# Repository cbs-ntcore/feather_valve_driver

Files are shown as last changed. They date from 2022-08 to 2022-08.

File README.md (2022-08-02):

Feather compatible 16 channel valve driver.

This was designed for 12 volt Lee valves.

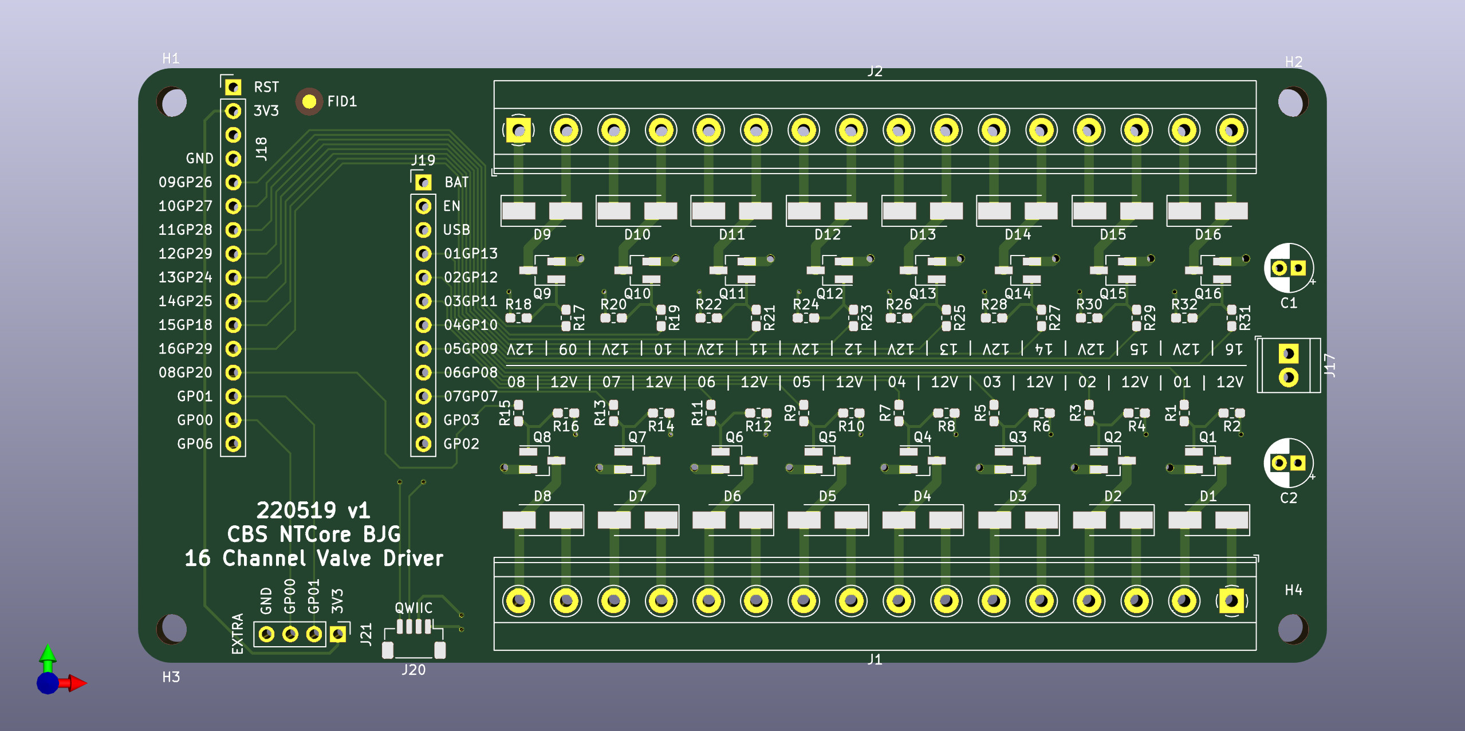
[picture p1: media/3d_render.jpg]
PCB 3D render


See [errata](/electronics/feather_valve_driver/ERRATA) for current minor electronic issues.

A simple 3d printed baseplate is included that supports the Lee valves:

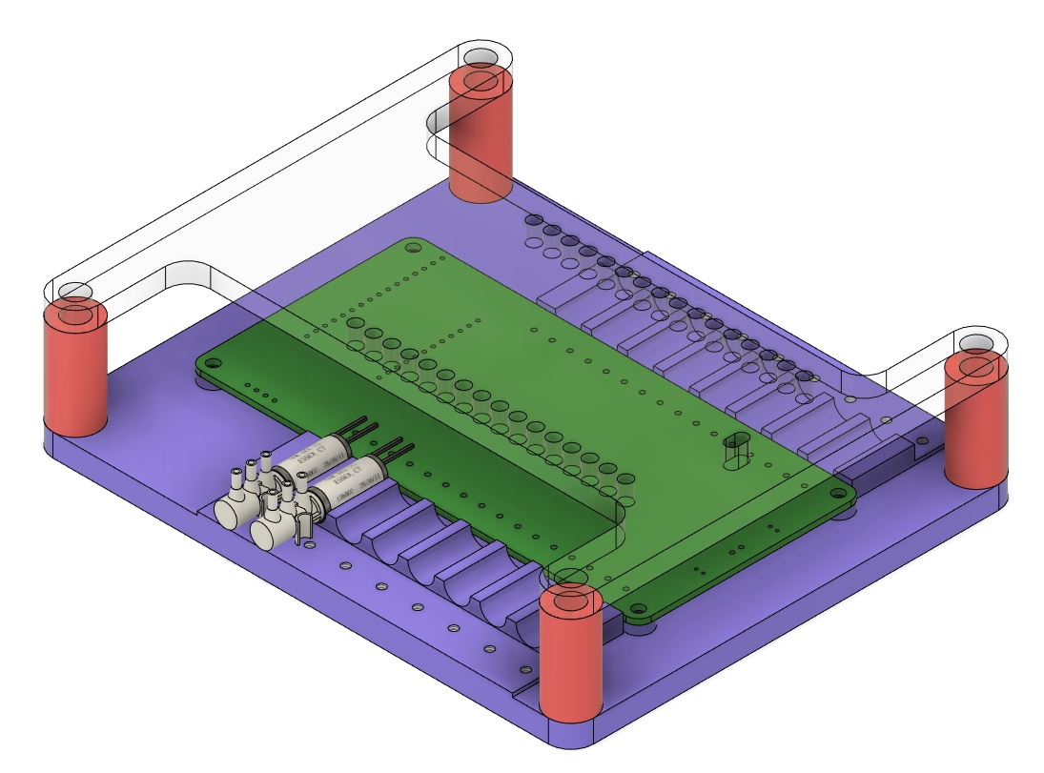
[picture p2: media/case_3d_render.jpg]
Baseplate 3D render


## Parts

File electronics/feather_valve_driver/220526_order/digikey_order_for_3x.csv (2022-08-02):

Index | Quantity | Part Number | Manufacturer Part Number | Description | Customer Reference | Available | Backorder | Unit Price | Extended Price USD
1 | 130 | 1655-S1MCT-ND | S1M | DIODE GEN PURP 1KV 1A SMA |  | 130 | 0 | 0.07000 | 9.10
2 | 130 | 31-DMN3731U-7CT-ND | DMN3731U-7 | MOSFET N-CH 30V 900MA SOT23 |  | 130 | 0 | 0.11850 | 15.41
3 | 130 | RMCF0603FT100RCT-ND | RMCF0603FT100R | RES 100 OHM 1% 1/10W 0603 |  | 130 | 0 | 0.00680 | 0.88
4 | 130 | RNCP0603FTD10K0CT-ND | RNCP0603FTD10K0 | RES 10K OHM 1% 1/8W 0603 |  | 130 | 0 | 0.02480 | 3.22
5 | 10 | A134903-ND | 1-282837-6 | TERM BLK 16P SIDE ENT 5.08MM PCB |  | 10 | 0 | 6.76200 | 67.62
6 | 10 | ED10561-ND | OSTVN02A150 | TERM BLK 2P SIDE ENT 2.54MM PCB |  | 10 | 0 | 0.59600 | 5.96
7 | 10 | 493-12902-1-ND | UVY1E101MDD1TD | CAP ALUM 100UF 20% 25V RADIAL |  | 10 | 0 | 0.27100 | 2.71

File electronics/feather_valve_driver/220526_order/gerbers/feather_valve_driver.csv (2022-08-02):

Id | Designator | Package | Quantity | Designation | Supplier and ref
1 | FID1 | Fiducial_1.5mm_Mask3mm | 1 | Fiducial
2 | H4,H3,H2,H1 | MountingHole_3.2mm_M3 | 4 | MountingHole
3 | C2,C1 | CP_Radial_D5.0mm_P2.00mm | 2 | CP
4 | J18 | PinHeader_1x16_P2.54mm_Vertical | 1 | Conn_01x16
5 | R32,R30,R28,R26,R24,R22,R20,R18,R16,R14,R12,R10,R8,R6,R4,R2 | R_0603_1608Metric_Pad1.05x0.95mm_HandSolder | 16 | 10k
6 | R31,R29,R27,R25,R23,R21,R19,R17,R15,R13,R11,R9,R7,R5,R3,R1 | R_0603_1608Metric_Pad1.05x0.95mm_HandSolder | 16 | 100
7 | Q16,Q15,Q14,Q13,Q12,Q11,Q10,Q9,Q8,Q7,Q6,Q5,Q4,Q3,Q2,Q1 | SOT-23_Handsoldering | 16 | Q_NMOS_GSD
8 | J21 | PinHeader_1x04_P2.54mm_Vertical | 1 | EXTRA
9 | J20 | JST_SH_BM04B-SRSS-TB_1x04-1MP_P1.00mm_Vertical | 1 | QWIIC
10 | J19 | PinHeader_1x12_P2.54mm_Vertical | 1 | Conn_01x12
11 | J17 | TerminalBlock_TE_282834-2_1x02_P2.54mm_Horizontal | 1 | Conn_01x02
12 | J2,J1 | TerminalBlock_Phoenix_MKDS-3-16-5.08_1x16_P5.08mm_Horizontal | 2 | Conn_01x16
13 | D16,D15,D14,D13,D12,D11,D10,D9,D8,D7,D6,D5,D4,D3,D2,D1 | D_SMA_Handsoldering | 16 | D

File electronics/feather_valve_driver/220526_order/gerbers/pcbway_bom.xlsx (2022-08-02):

 |  |  | xxxx xxxx xxxxx xxPCS BOM (Sample Bill of Materials)
Item # | *Designator | *Qty | Manufacturer | *Mfg Part # | Description / Value | *Package/Footprint | Type | Your Instructions / Notes
1 | FID1 | 1 |  | DNP |  | DNP |  | Do not place
2 | H4,H3,H2,H1 | 4 |  | DNP |  | DNP |  | Do not place
3 | C2,C1 | 2 |  | DNP |  | DNP |  | Do not place
4 | J18 | 1 |  | DNP |  | DNP |  | Do not place
5 | R32,R30,R28,R26,R24,R22,R20,R18,R16,R14,R12,R10,R8,R6,R4,R2 | 16 | any/open | any/open | 10k Ohm 1% 1/8W 0603 | 0603
6 | R31,R29,R27,R25,R23,R21,R19,R17,R15,R13,R11,R9,R7,R5,R3,R1 | 16 | any/open | any/open | 100 Ohm 1% 1/8W 0603 | 0603
7 | Q16,Q15,Q14,Q13,Q12,Q11,Q10,Q9,Q8,Q7,Q6,Q5,Q4,Q3,Q2,Q1 | 16 | Diodes Incorporated | DMN3731U | 30V n-channel enhancement mode mosfet | SOT-23 |  | 0.95V Gate threshold 560 mOhm on resistance
8 | J21 | 1 |  | DNP |  | DNP |  | Do not place
9 | J20 | 1 |  | DNP |  | DNP |  | Do not place
10 | J19 | 1 |  | DNP |  | DNP |  | Do not place
11 | J17 | 1 |  | DNP |  | DNP |  | Do not place
12 | J2,J1 | 2 |  | DNP |  | DNP |  | Do not place
13 | D16,D15,D14,D13,D12,D11,D10,D9,D8,D7,D6,D5,D4,D3,D2,D1 | 16 | SMC Diode Solutions | SM1 | DIODE GEN PURP 1KV 1A SMA | SMA
Need a quick and accurante quote? Need an efficient production? Please read SMT Ordering Necessary Files & Info in 1 minute. Thank you very much! (https://www.pcbway.com/smt_ordering_guide.html)
Click for Instructions on How to Create a BOM (https://www.pcbway.com/blog/PCB_Assembly/How_to_Build_a_BOM__Bill_Of_Materials_.html)

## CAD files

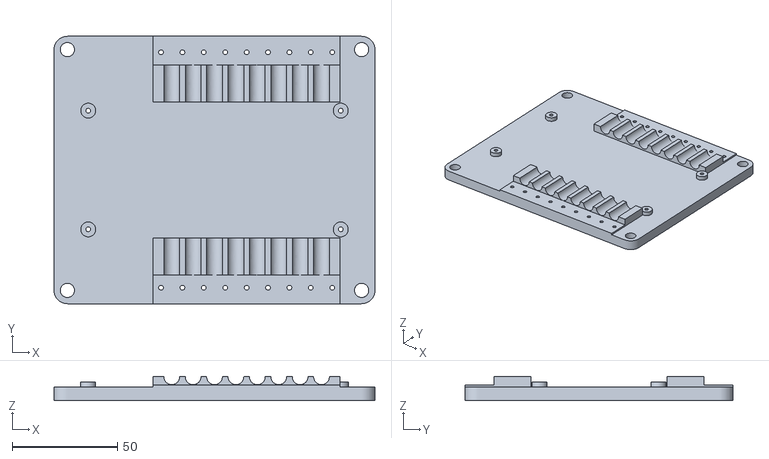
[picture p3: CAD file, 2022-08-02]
hardware/leevalve_baseplate.stl
152.4 x 127.0 x 11.4

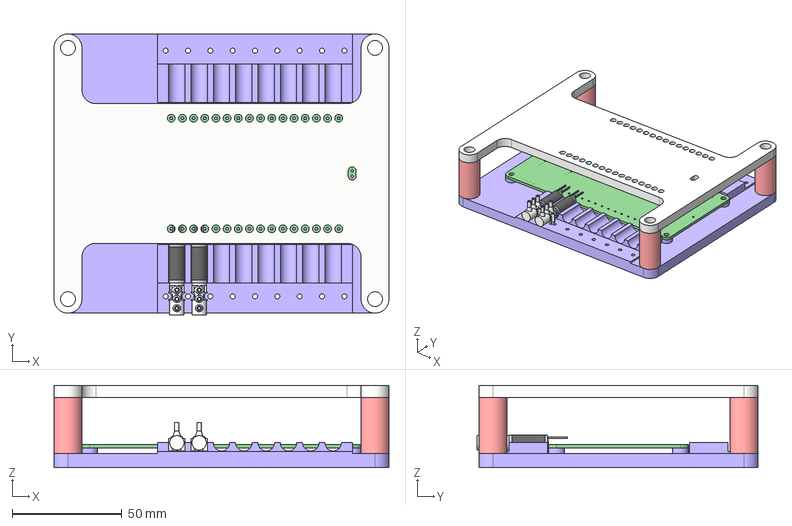
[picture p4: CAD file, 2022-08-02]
hardware/feather_valve_driver v14.step
152.4 x 127.9 x 37.3 mm
_autosave-feather_valve_driver PCB
LHDA0533115H v3 x 2
spacer
acrylic top plate

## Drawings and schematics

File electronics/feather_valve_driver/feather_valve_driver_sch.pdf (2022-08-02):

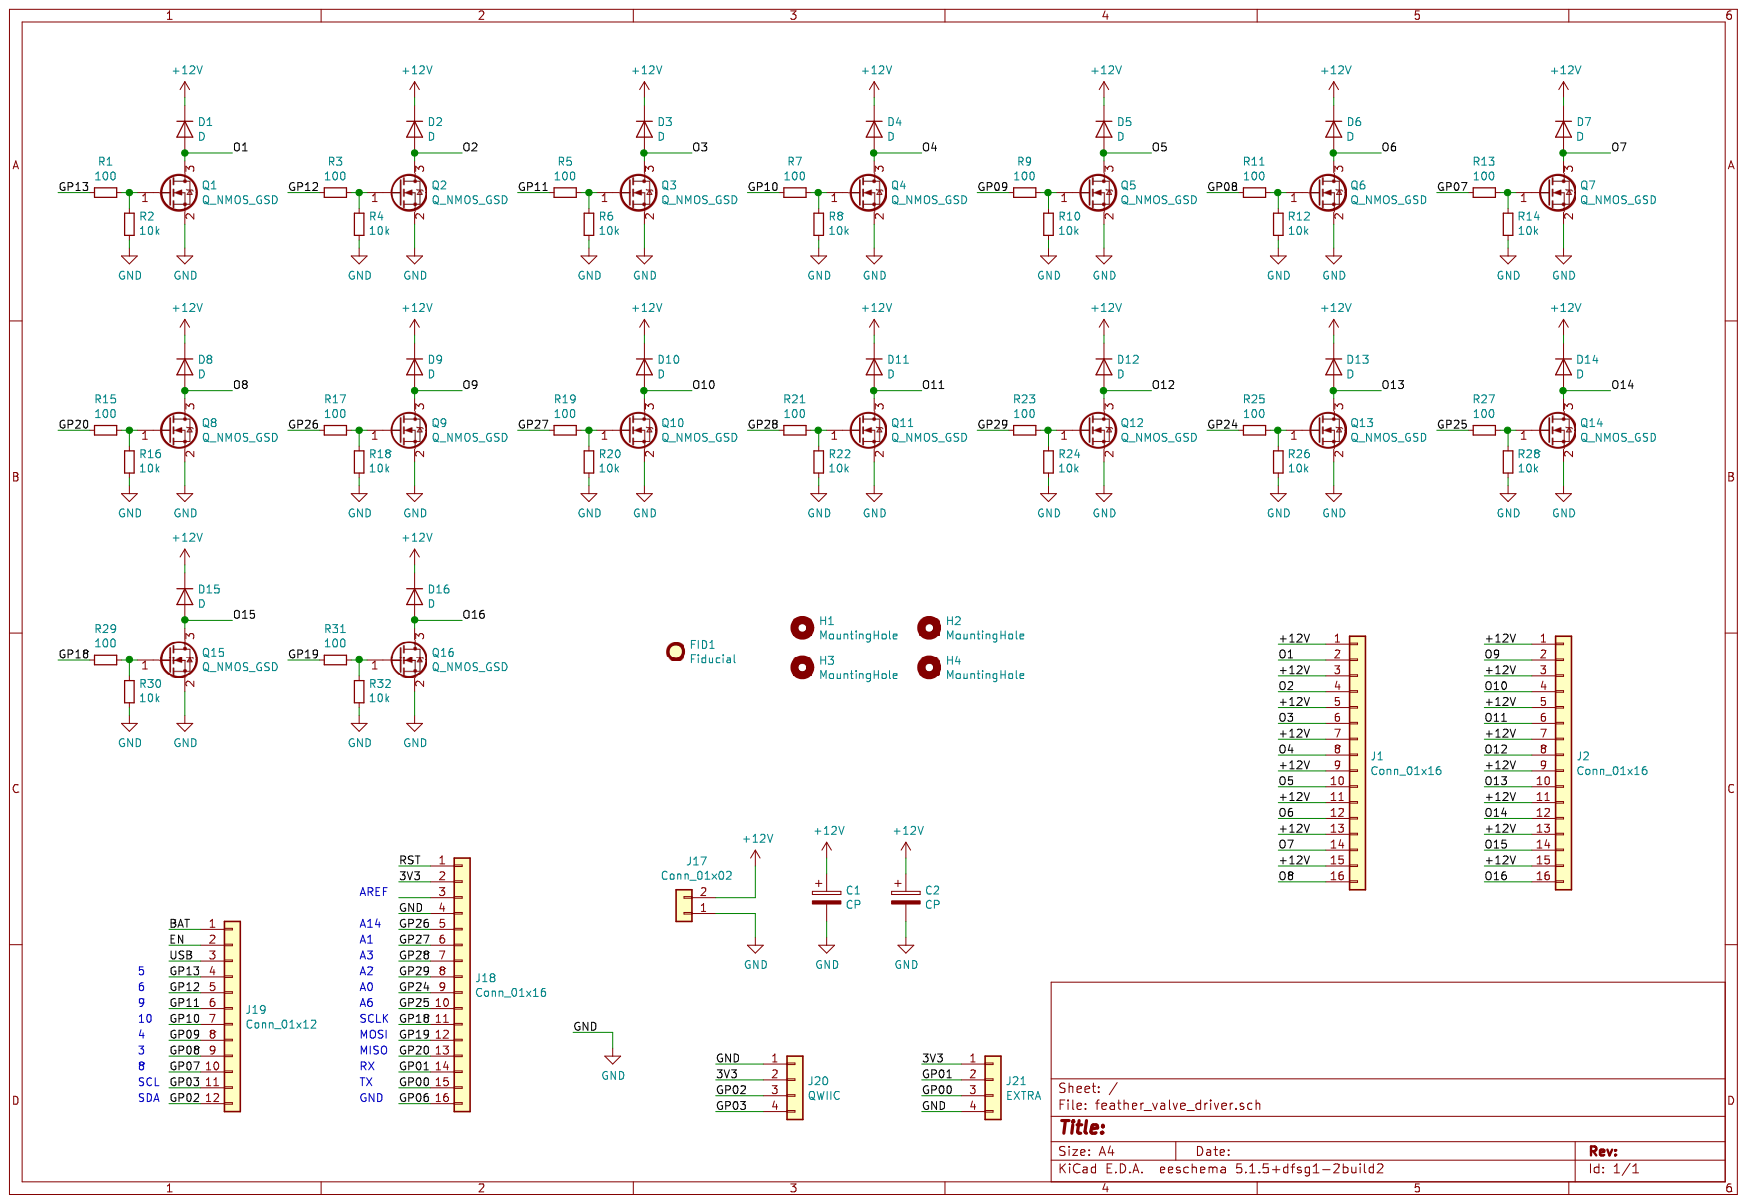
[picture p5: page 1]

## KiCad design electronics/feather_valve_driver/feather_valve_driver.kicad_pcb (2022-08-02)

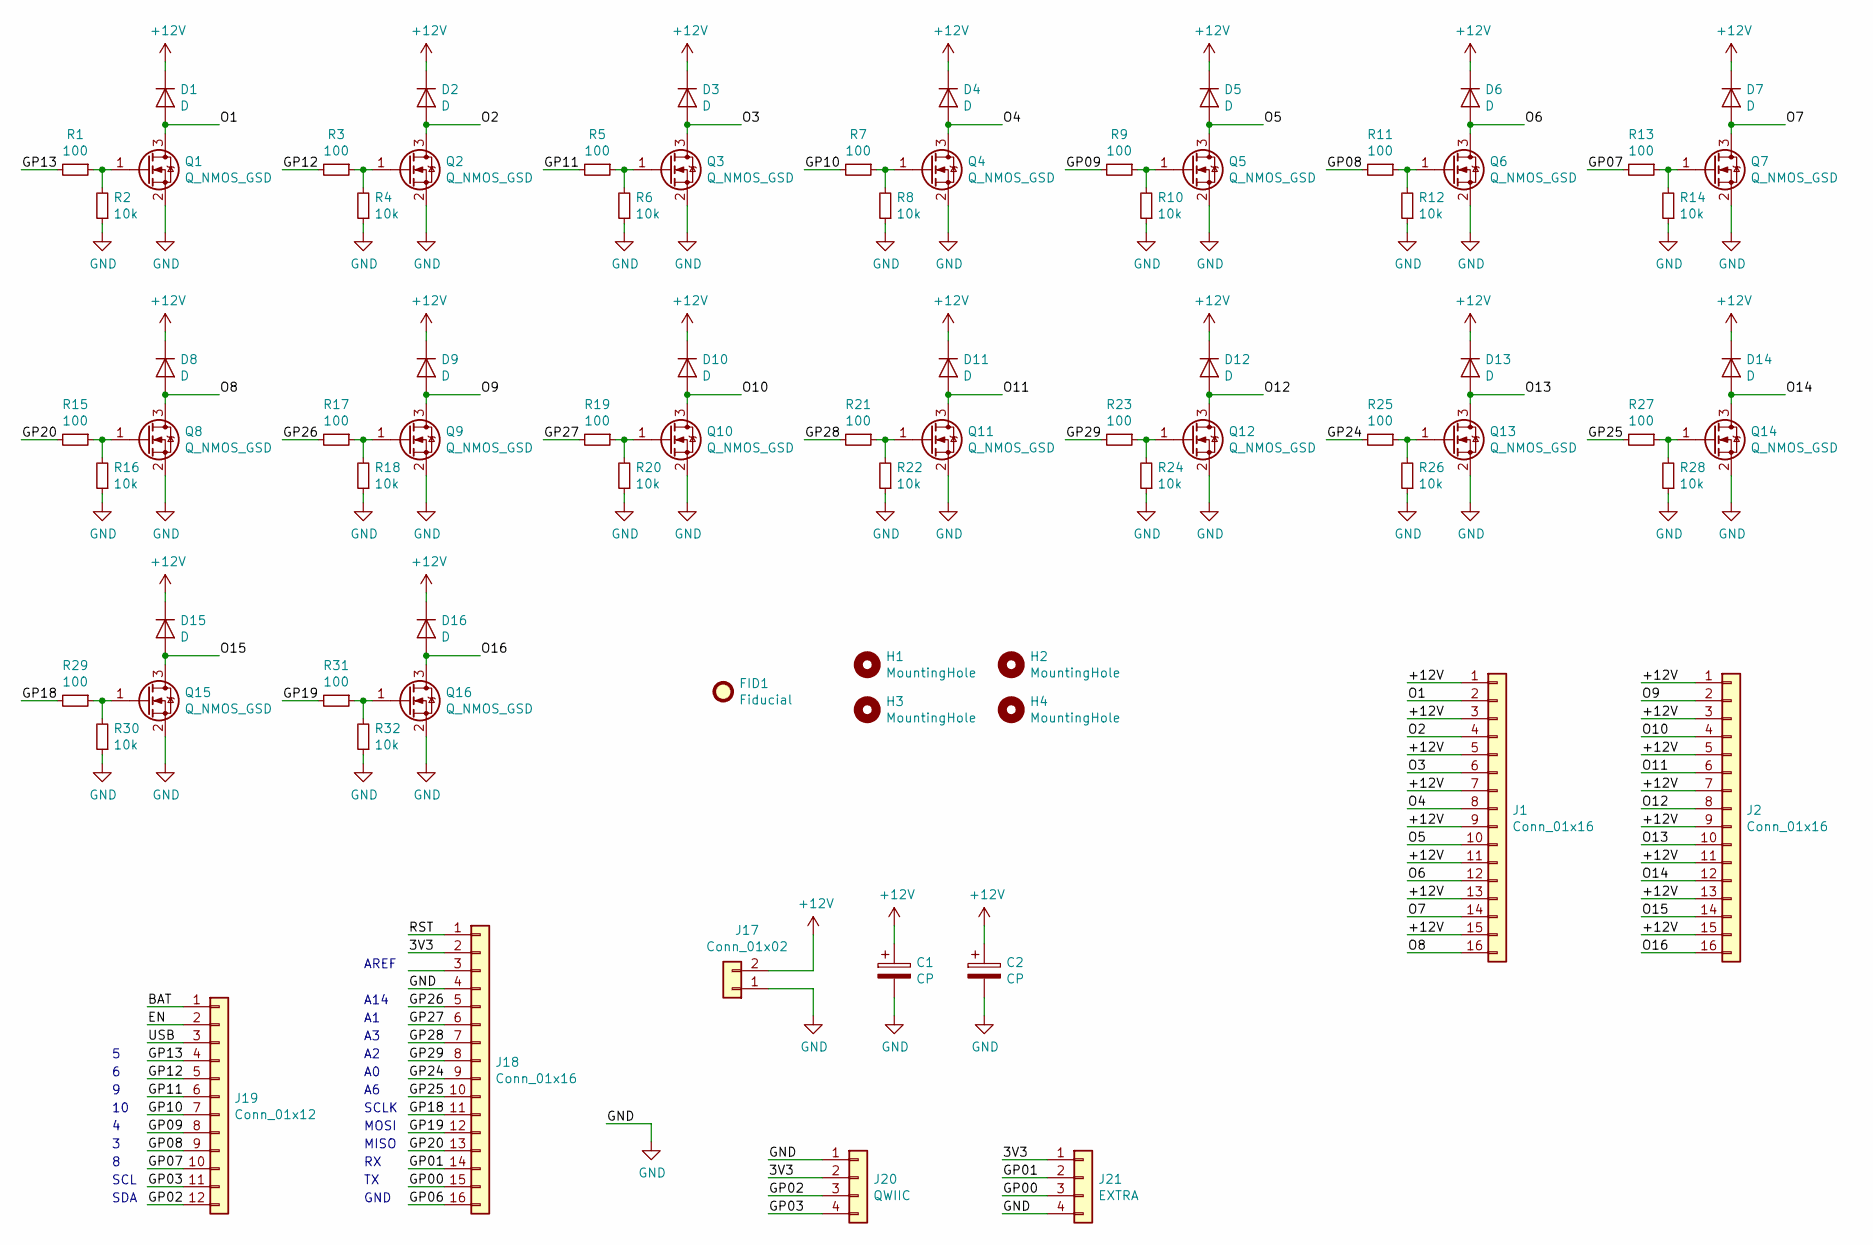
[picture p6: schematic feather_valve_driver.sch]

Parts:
C1, C2: CP; CP_Radial_D5.0mm_P2.00mm
D1, D2, D3, D4, D5, D6, D7, D8, D9, D10, D11, D12, D13, D14, D15, D16: D; D_SMA_Handsoldering
FID1: Fiducial; Fiducial_1.5mm_Mask3mm
H1, H2, H3, H4: MountingHole; MountingHole_3.2mm_M3
J1, J2: Conn_01x16; TerminalBlock_Phoenix_MKDS-1,5-16-5.08_1x16_P5.08mm_Horizon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
J17: Conn_01x02; TerminalBlock_TE_282834-2_1x02_P2.54mm_Horizontal
J18: Conn_01x16; PinHeader_1x16_P2.54mm_Vertical
J19: Conn_01x12; PinHeader_1x12_P2.54mm_Vertical
J20: QWIIC; JST_SH_BM04B-SRSS-TB_1x04-1MP_P1.00mm_Vertical
J21: EXTRA; PinHeader_1x04_P2.54mm_Vertical
Q1, Q2, Q3, Q4, Q5, Q6, Q7, Q8, Q9, Q10, Q11, Q12, Q13, Q14, Q15, Q16: Q_NMOS_GSD; SOT-23_Handsoldering
R1, R3, R5, R7, R9, R11, R13, R15, R17, R19, R21, R23, R25, R27, R29, R31: 100; R_0603_1608Metric_Pad1.05x0.95mm_HandSolder
R2, R4, R6, R8, R10, R12, R14, R16, R18, R20, R22, R24, R26, R28, R30, R32: 10k; R_0603_1608Metric_Pad1.05x0.95mm_HandSolder

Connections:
+12V: C1.1, C2.1, D1.1 (K), D2.1 (K), D3.1 (K), D4.1 (K), D5.1 (K), D6.1 (K), D7.1 (K), D8.1 (K), D9.1 (K), D10.1 (K), D11.1 (K), D12.1 (K), D13.1 (K), D14.1 (K), D15.1 (K), D16.1 (K), J1.1, J1.3, J1.5, J1.7, J1.9, J1.11, J1.13, J1.15, J2.1, J2.3, J2.5, J2.7, J2.9, J2.11, J2.13, J2.15, J17.2
/3V3: J18.2, J20.2, J21.1
/BAT: J19.1
/EN: J19.2
/GP00: J18.15, J21.3
/GP01: J18.14, J21.2
/GP02: J19.12, J20.3
/GP03: J19.11, J20.4
/GP06: J18.16
/GP07: J19.10, R13.2
/GP08: J19.9, R11.2
/GP09: J19.8, R9.2
/GP10: J19.7, R7.2
/GP11: J19.6, R5.2
/GP12: J19.5, R3.2
/GP13: J19.4, R1.2
/GP18: J18.11, R29.2
/GP19: J18.12, R31.2
/GP20: J18.13, R15.2
/GP24: J18.9, R25.2
/GP25: J18.10, R27.2
/GP26: J18.5, R17.2
/GP27: J18.6, R19.2
/GP28: J18.7, R21.2
/GP29: J18.8, R23.2
/O1: D1.2 (A), J1.2, Q1.3 (D)
/O2: D2.2 (A), J1.4, Q2.3 (D)
/O3: D3.2 (A), J1.6, Q3.3 (D)
/O4: D4.2 (A), J1.8, Q4.3 (D)
/O5: D5.2 (A), J1.10, Q5.3 (D)
/O6: D6.2 (A), J1.12, Q6.3 (D)
/O7: D7.2 (A), J1.14, Q7.3 (D)
/O8: D8.2 (A), J1.16, Q8.3 (D)
/O9: D9.2 (A), J2.2, Q9.3 (D)
/O10: D10.2 (A), J2.4, Q10.3 (D)
/O11: D11.2 (A), J2.6, Q11.3 (D)
/O12: D12.2 (A), J2.8, Q12.3 (D)
/O13: D13.2 (A), J2.10, Q13.3 (D)
/O14: D14.2 (A), J2.12, Q14.3 (D)
/O15: D15.2 (A), J2.14, Q15.3 (D)
/O16: D16.2 (A), J2.16, Q16.3 (D)
/RST: J18.1
/USB: J19.3
GND: C1.2, C2.2, J17.1, J18.4, J20.1, J21.4, Q1.2 (S), Q2.2 (S), Q3.2 (S), Q4.2 (S), Q5.2 (S), Q6.2 (S), Q7.2 (S), Q8.2 (S), Q9.2 (S), Q10.2 (S), Q11.2 (S), Q12.2 (S), Q13.2 (S), Q14.2 (S), Q15.2 (S), Q16.2 (S), R2.1, R4.1, R6.1, R8.1, R10.1, R12.1, R14.1, R16.1, R18.1, R20.1, R22.1, R24.1, R26.1, R28.1, R30.1, R32.1
unnamed: Q1.1 (G), R1.1, R2.2
unnamed: Q2.1 (G), R3.1, R4.2
unnamed: Q3.1 (G), R5.1, R6.2
unnamed: Q4.1 (G), R7.1, R8.2
unnamed: Q5.1 (G), R9.1, R10.2
unnamed: Q6.1 (G), R11.1, R12.2
unnamed: Q7.1 (G), R13.1, R14.2
unnamed: Q8.1 (G), R15.1, R16.2
unnamed: Q9.1 (G), R17.1, R18.2
unnamed: Q10.1 (G), R19.1, R20.2
unnamed: Q11.1 (G), R21.1, R22.2
unnamed: Q12.1 (G), R23.1, R24.2
unnamed: Q13.1 (G), R25.1, R26.2
unnamed: Q14.1 (G), R27.1, R28.2
unnamed: Q15.1 (G), R29.1, R30.2
unnamed: Q16.1 (G), R31.1, R32.2

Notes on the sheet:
SDA
SCL
GND
MISO
MOSI
SCLK
A14
AREF

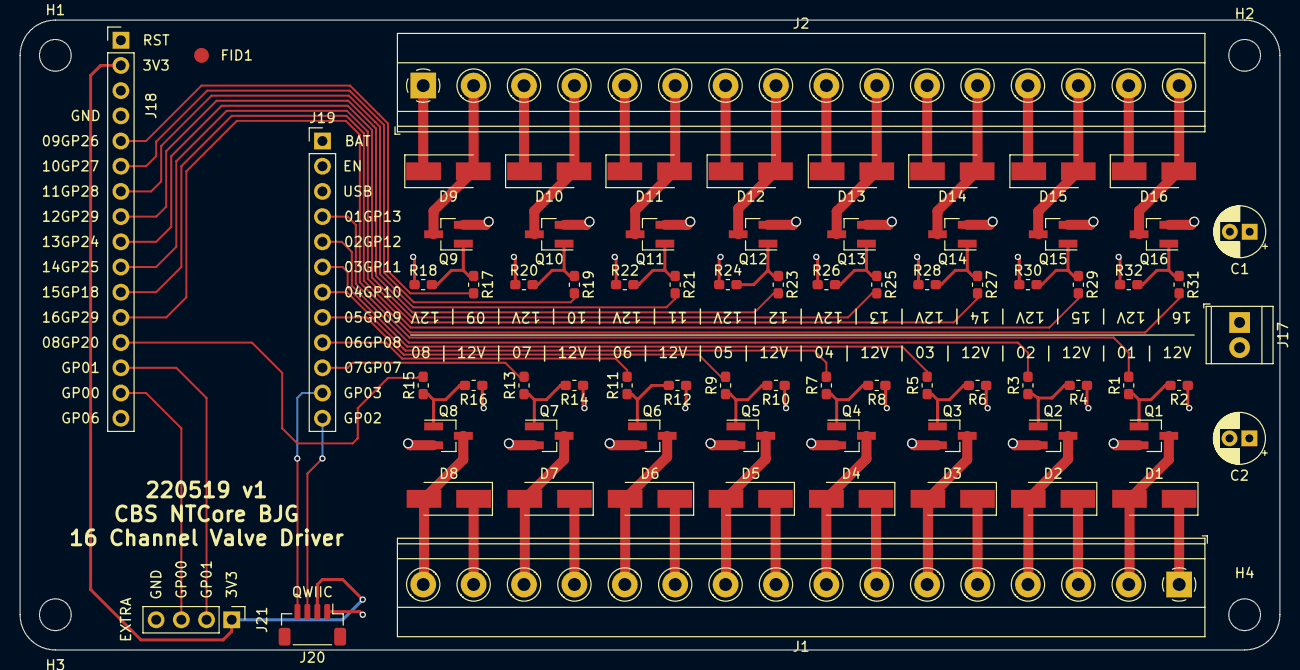
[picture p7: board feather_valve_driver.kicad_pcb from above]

Board: 2 copper layers, 127.0 x 63.5 mm, 78 parts (0 on the bottom side), 55 nets.
